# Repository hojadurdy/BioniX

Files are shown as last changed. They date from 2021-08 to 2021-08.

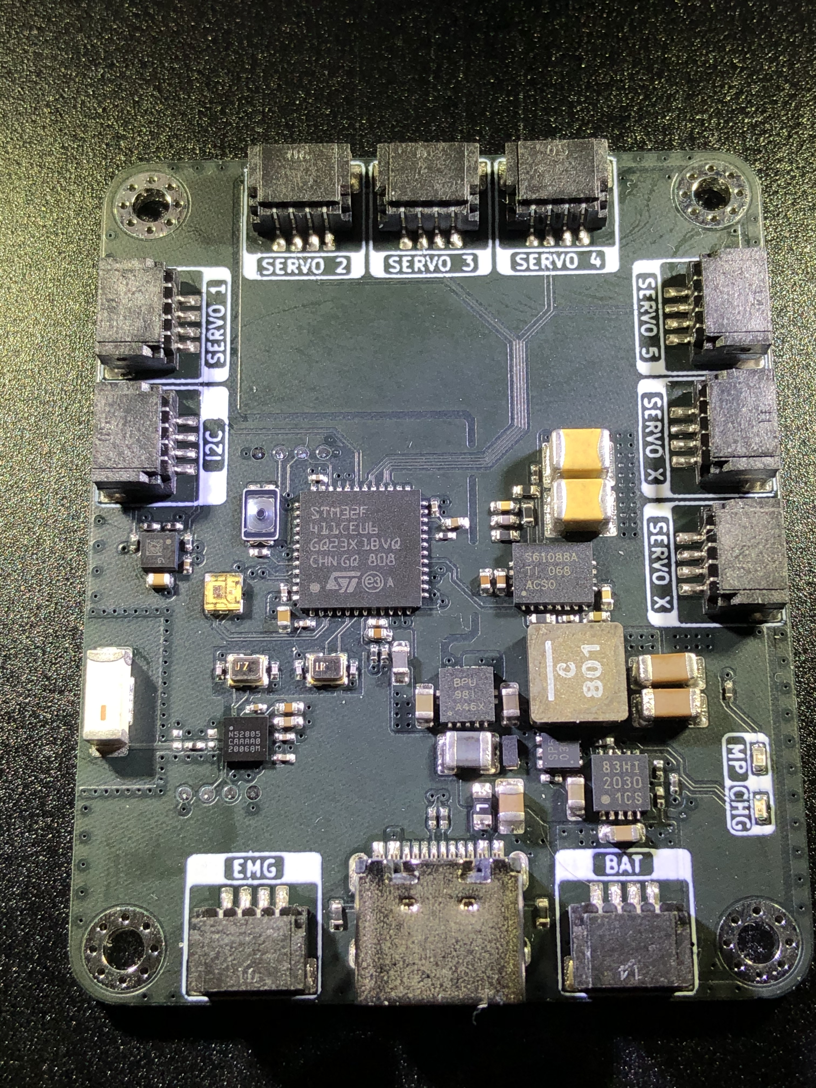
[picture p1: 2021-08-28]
Photo/IMG_0271.jpeg

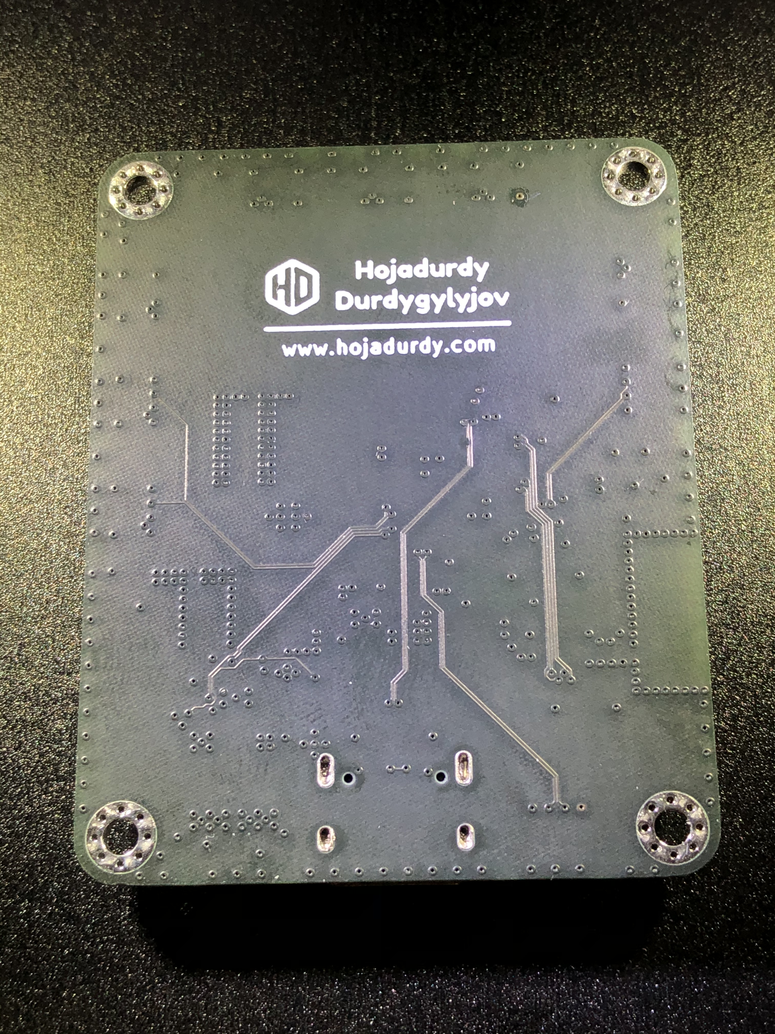
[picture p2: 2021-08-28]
Photo/IMG_0272.jpeg

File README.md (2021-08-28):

### BioniX
Controller board for a prototype robotic prosthetic hand. 

#Features

- 5 servo motors. 1 for each finger.
- 2 servo motors for wrist gimbal.
- Onboard accelerometer and gyro.
- nRF805 Bleetooth SoC to communicate with mobile app.
- 600mA Li-Ion battery charging.
- 3.3V@1A Buck-Boost converter for EMG sensor and for the rest of the board.
- 6V@4A Boost converter for servos.

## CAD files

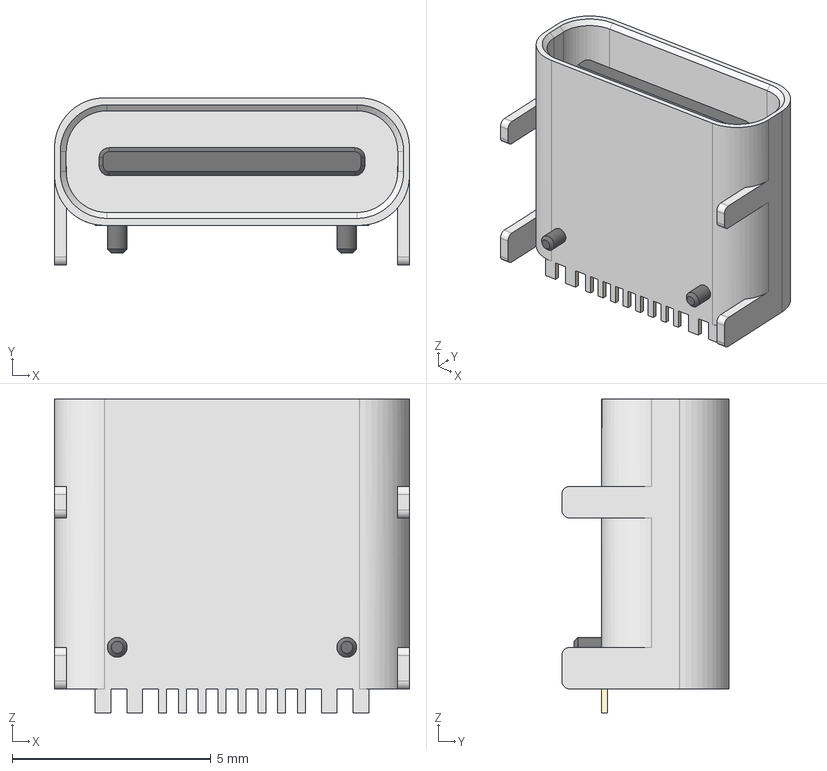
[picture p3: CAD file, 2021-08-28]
3D/TYPE-C Female Connector.step
8.94 x 4.21 x 7.90 mm

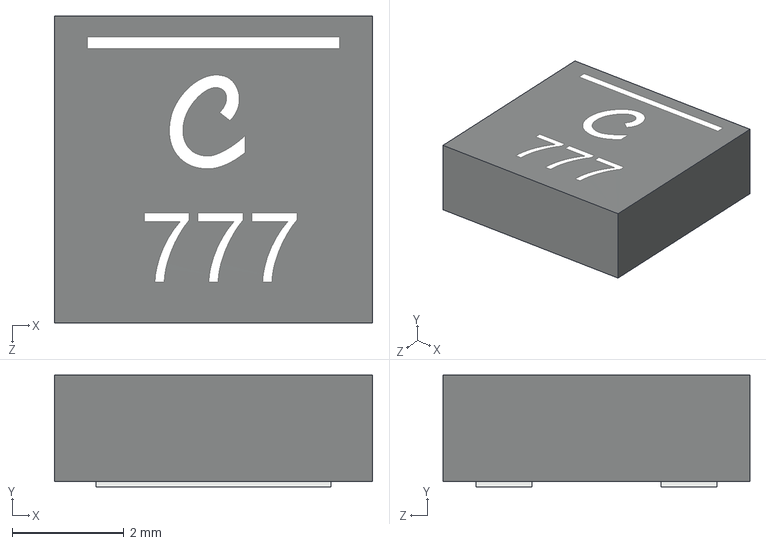
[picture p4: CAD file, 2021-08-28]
3D/Coilcraft-XAL5020.step
5.68 x 2.00 x 5.48 mm

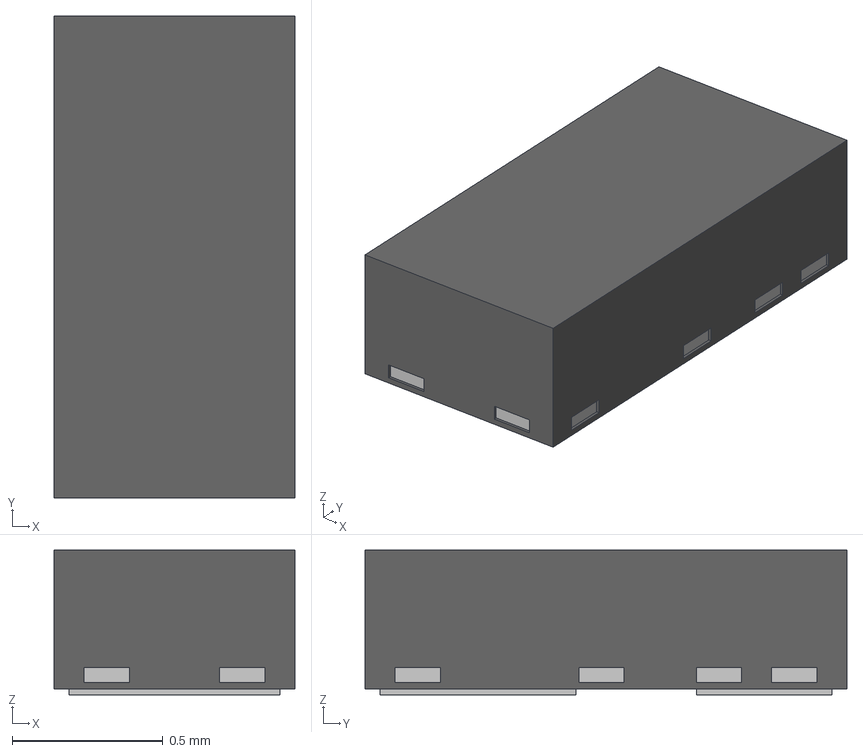
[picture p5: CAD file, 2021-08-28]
3D/CST2C.STEP
0.8 x 1.60 x 0.48 mm

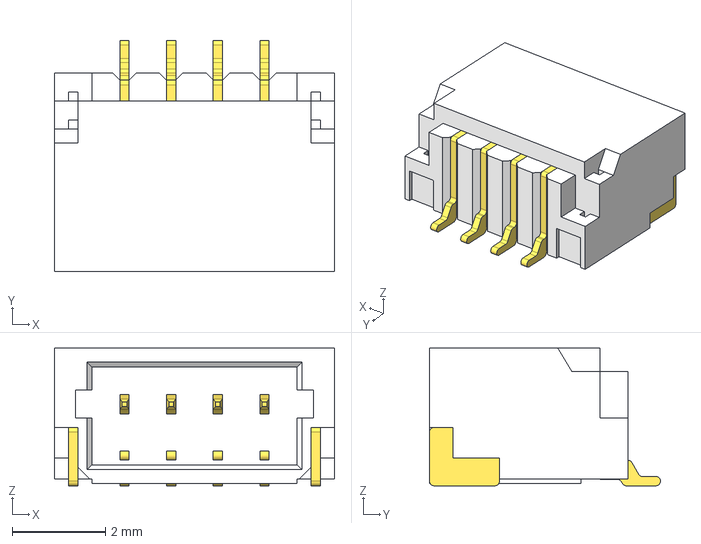
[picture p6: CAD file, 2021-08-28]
3D/JST-SH_4Pin_P1mm.step
6.00 x 4.95 x 2.95 mm

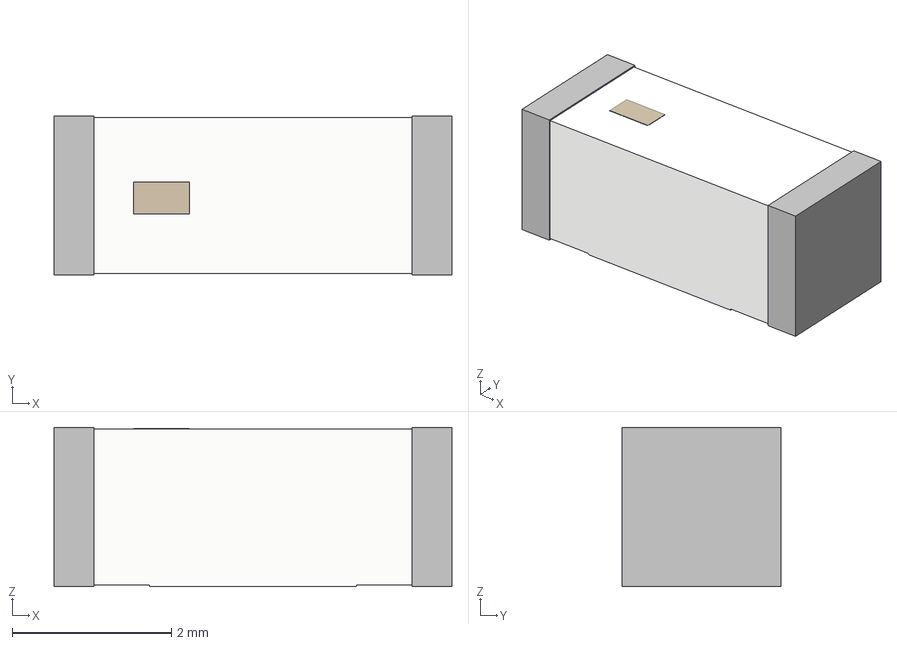
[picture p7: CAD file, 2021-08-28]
3D/2450AT42B100E.step
5.00 x 2.00 x 2.00 mm

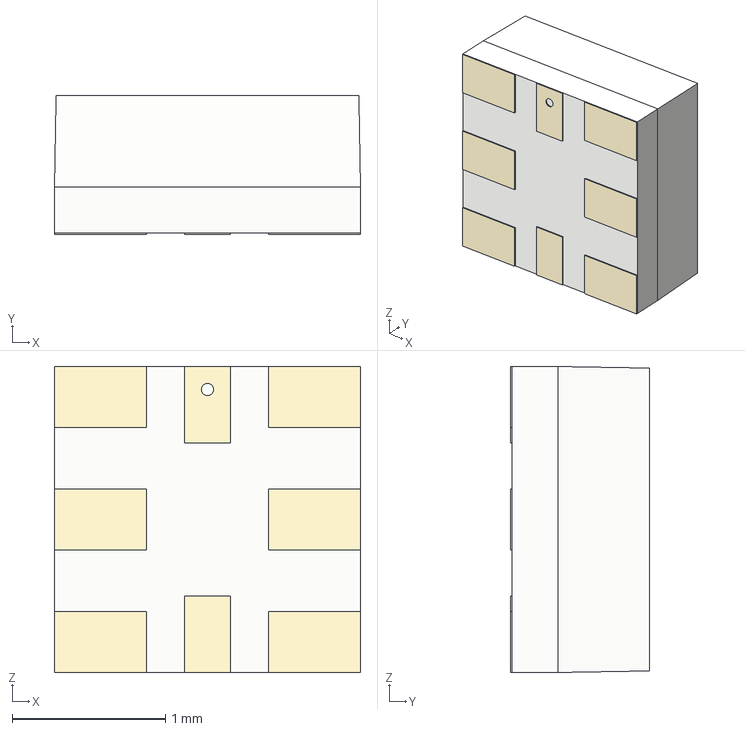
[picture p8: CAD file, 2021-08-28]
3D/APA102 2020 LED.step
2.00 x 0.91 x 2.00 mm

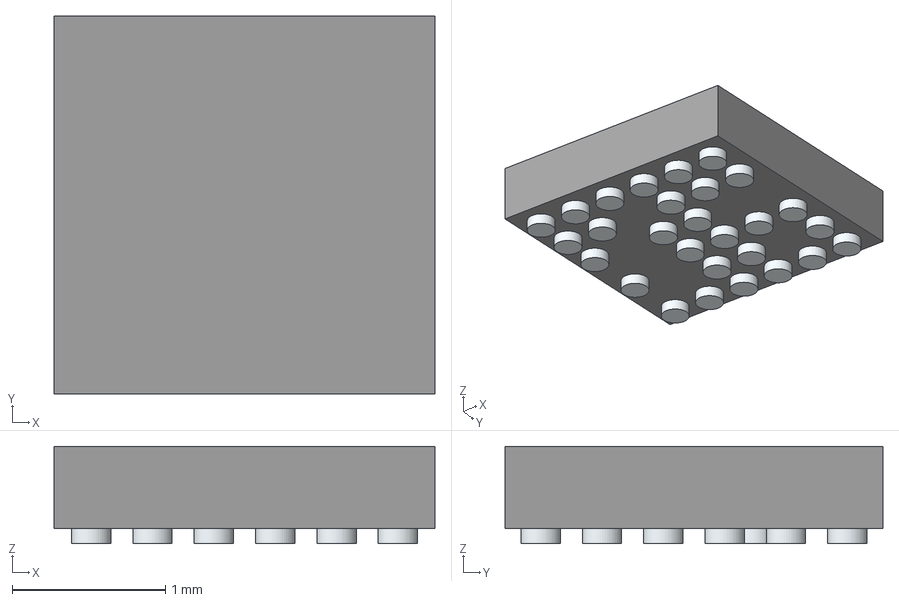
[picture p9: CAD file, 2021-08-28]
3D/NRF52805-CAAA.step
2.48 x 2.46 x 0.635 mm
Pins

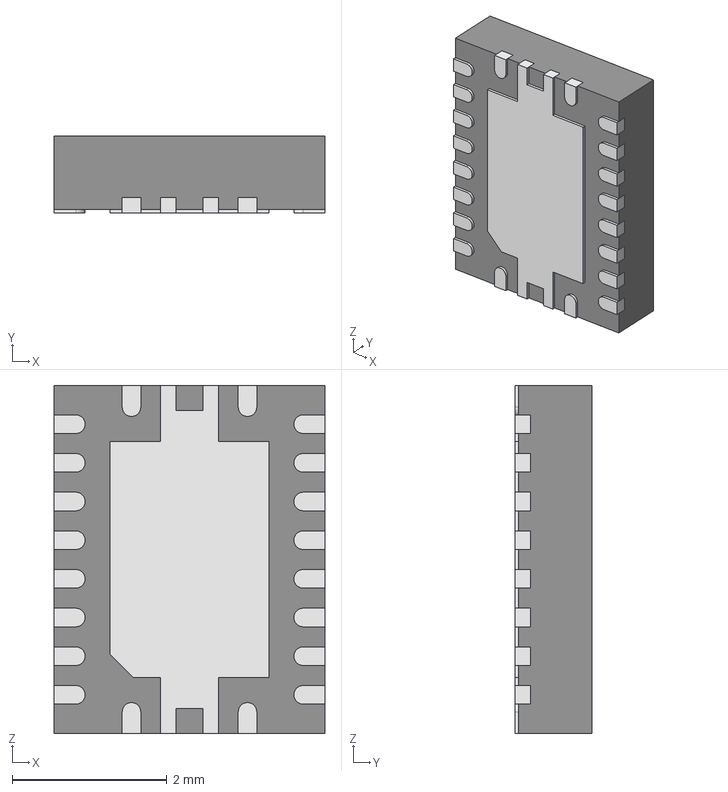
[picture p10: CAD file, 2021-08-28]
3D/TPS61088RHLT.STEP
3.50 x 1.00 x 4.50 mm

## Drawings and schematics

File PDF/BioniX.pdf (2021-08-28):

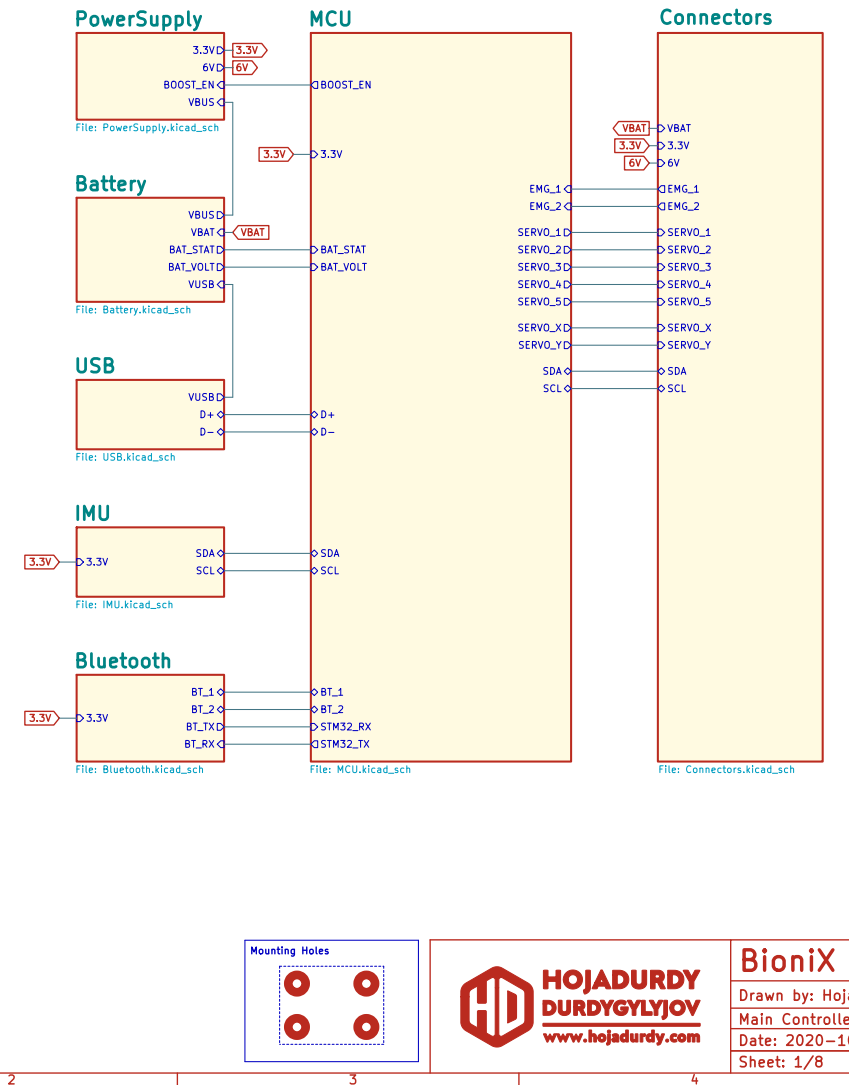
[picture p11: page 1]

File: BioniX.kicad_sch Sheet: 1/8 Drawn by: Hojadurdy Durdygylyjov Main Controller Board for BioniX Prosthetic Arm with Linear Actuators. License: CC Attribution-ShareAlike 4.0 International MCU
BAT_VOLT BAT_STAT
SCL VUSB
File: USB.kicad_sch Bluetooth

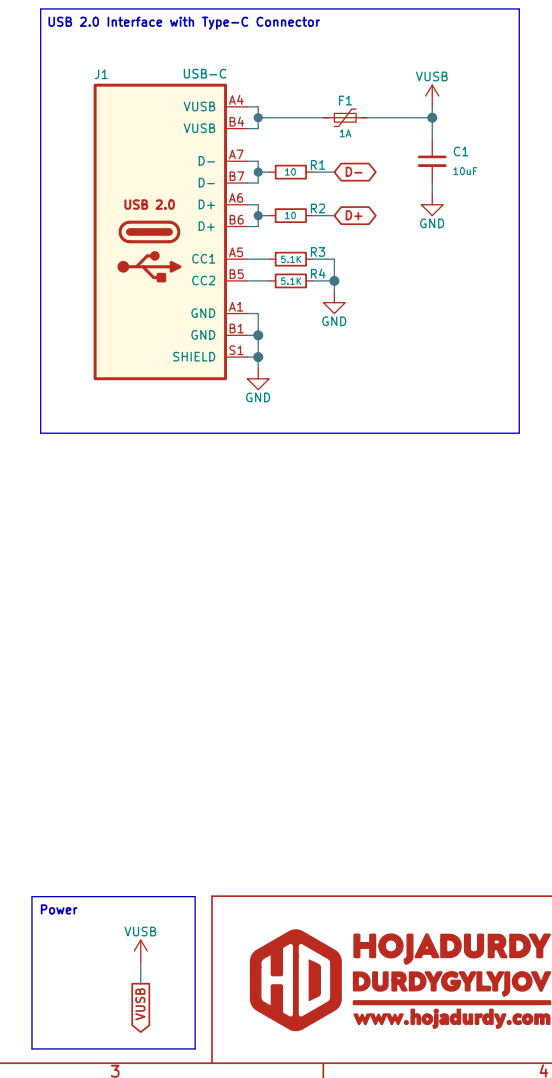
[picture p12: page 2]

USB 2.0 Interface with Type-C Connector
R1 10 GND
D- D+ Power

File: USB.kicad_sch Sheet: 2/8 Drawn by: Hojadurdy Durdygylyjov
USB 2.0 Interface with Type-C Connector License: CC Attribution-ShareAlike 4.0 International

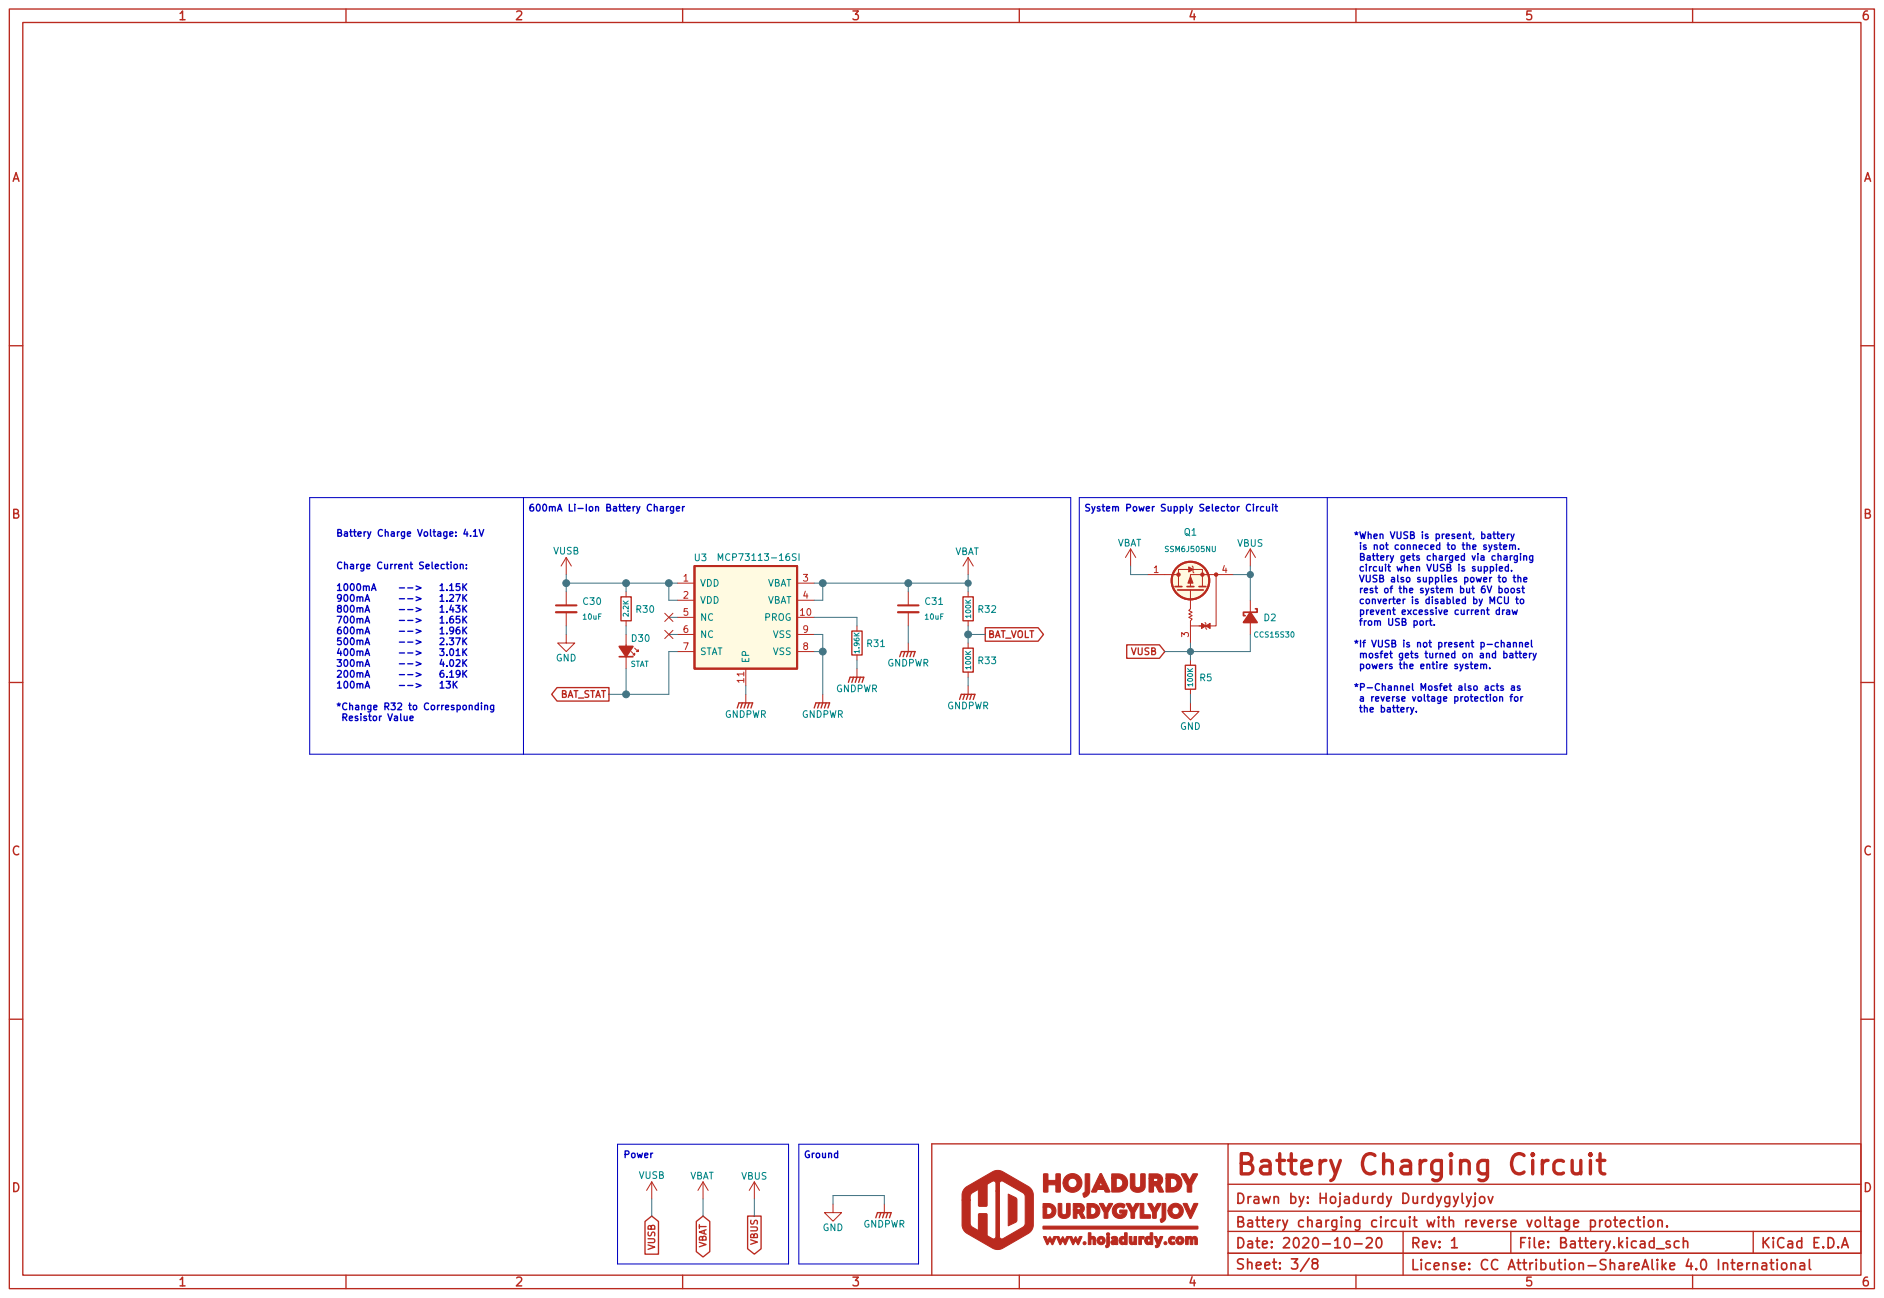
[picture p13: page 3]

the battery. 600mA Li-Ion Battery Charger Power

Battery Charge Voltage: 4.1V Charge Current Selection: 1000mA --> 1.15K

is not conneced to the system.
Battery gets charged via charging
circuit when VUSB is suppied.
VUSB also supplies power to the
rest of the system but 6V boost
converter is disabled by MCU to
prevent excessive current draw
from USB port. *If VUSB is not present p-channel

mosfet gets turned on and battery
powers the entire system. *P-Channel Mosfet also acts as

a reverse voltage protection for

File: Battery.kicad_sch Sheet: 3/8 Drawn by: Hojadurdy Durdygylyjov
Battery charging circuit with reverse voltage protection. License: CC Attribution-ShareAlike 4.0 International

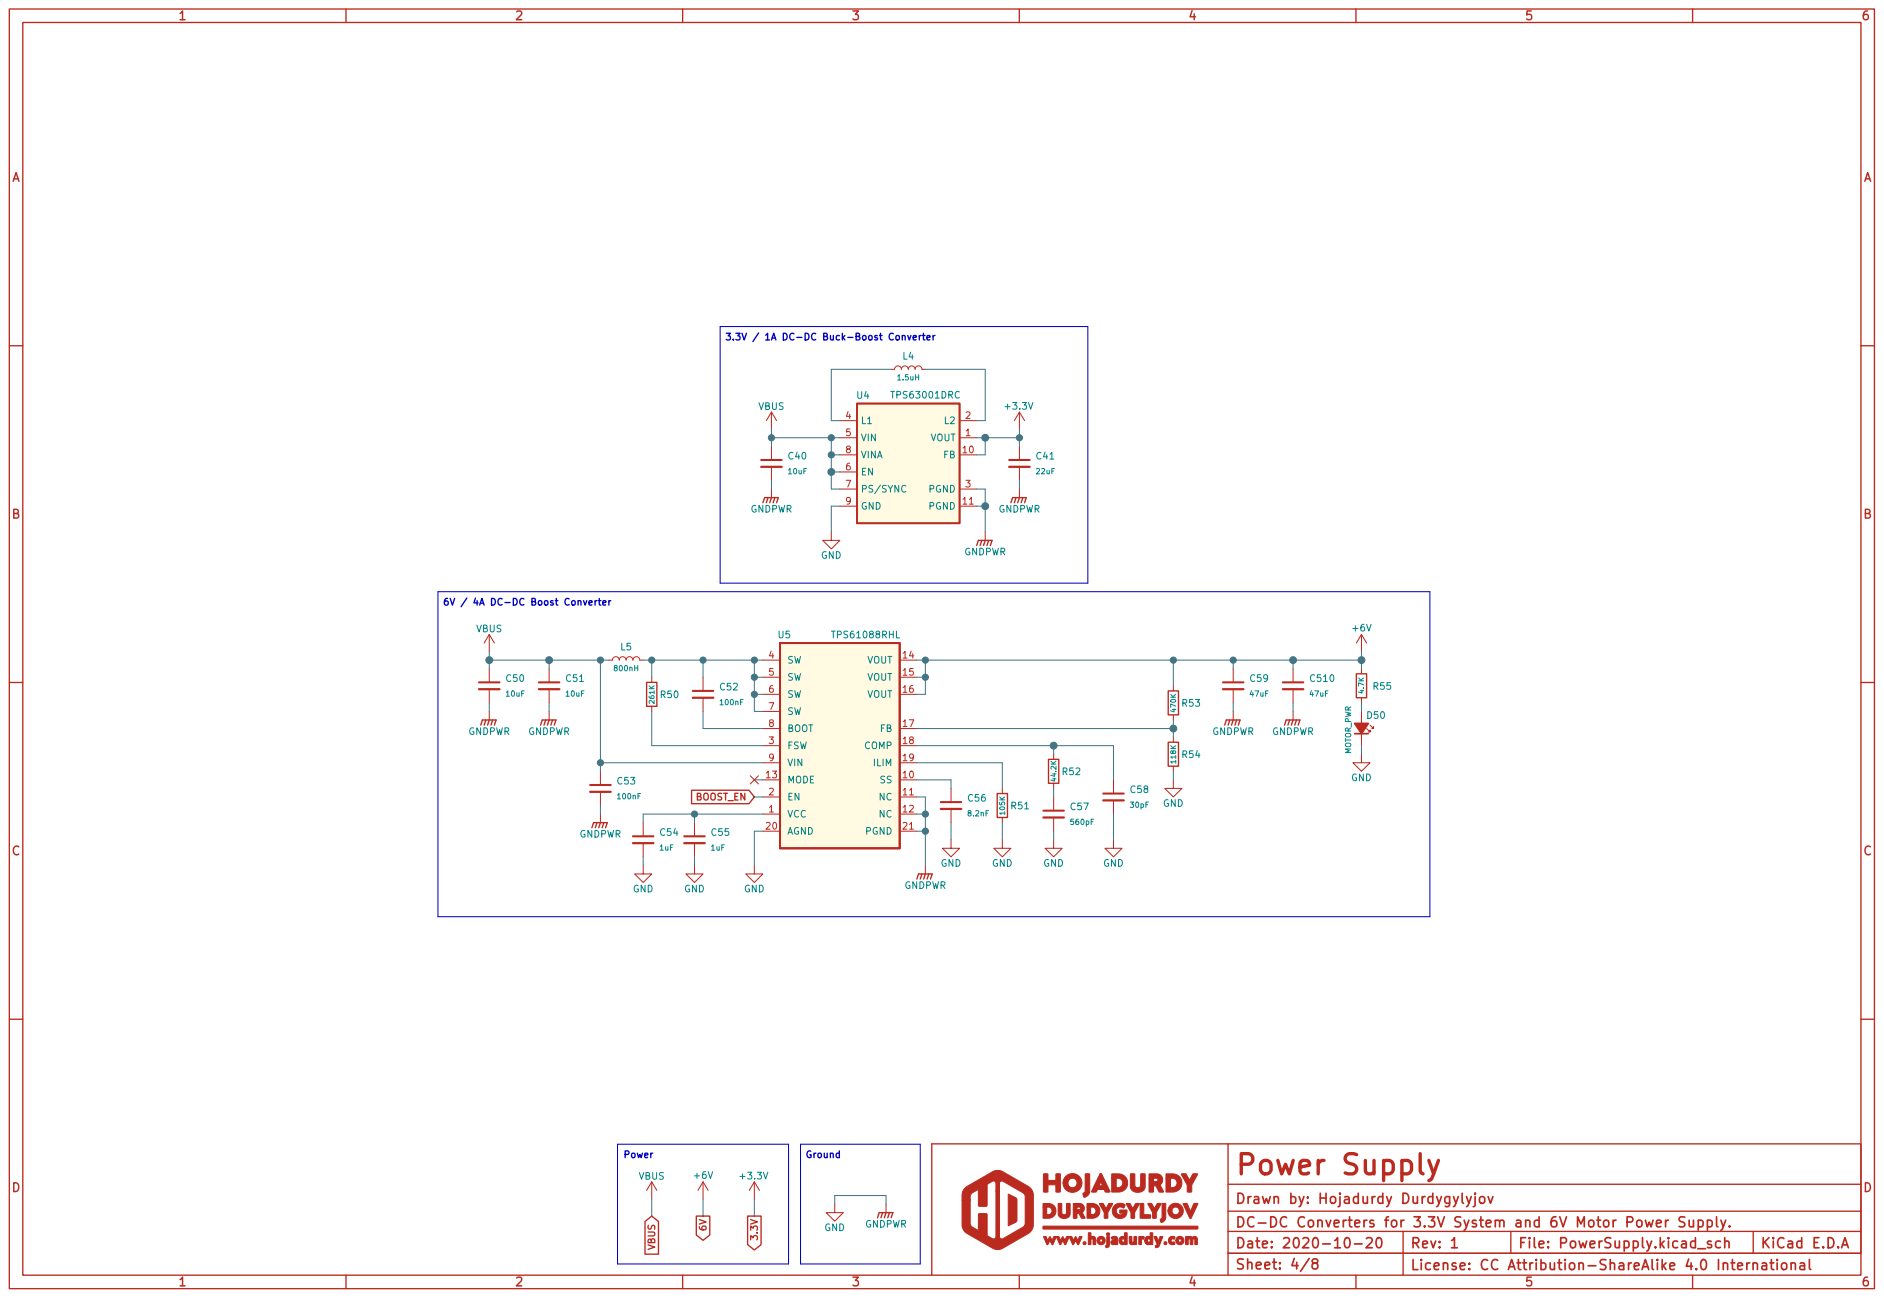
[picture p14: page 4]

File: PowerSupply.kicad_sch Sheet: 4/8 Drawn by: Hojadurdy Durdygylyjov

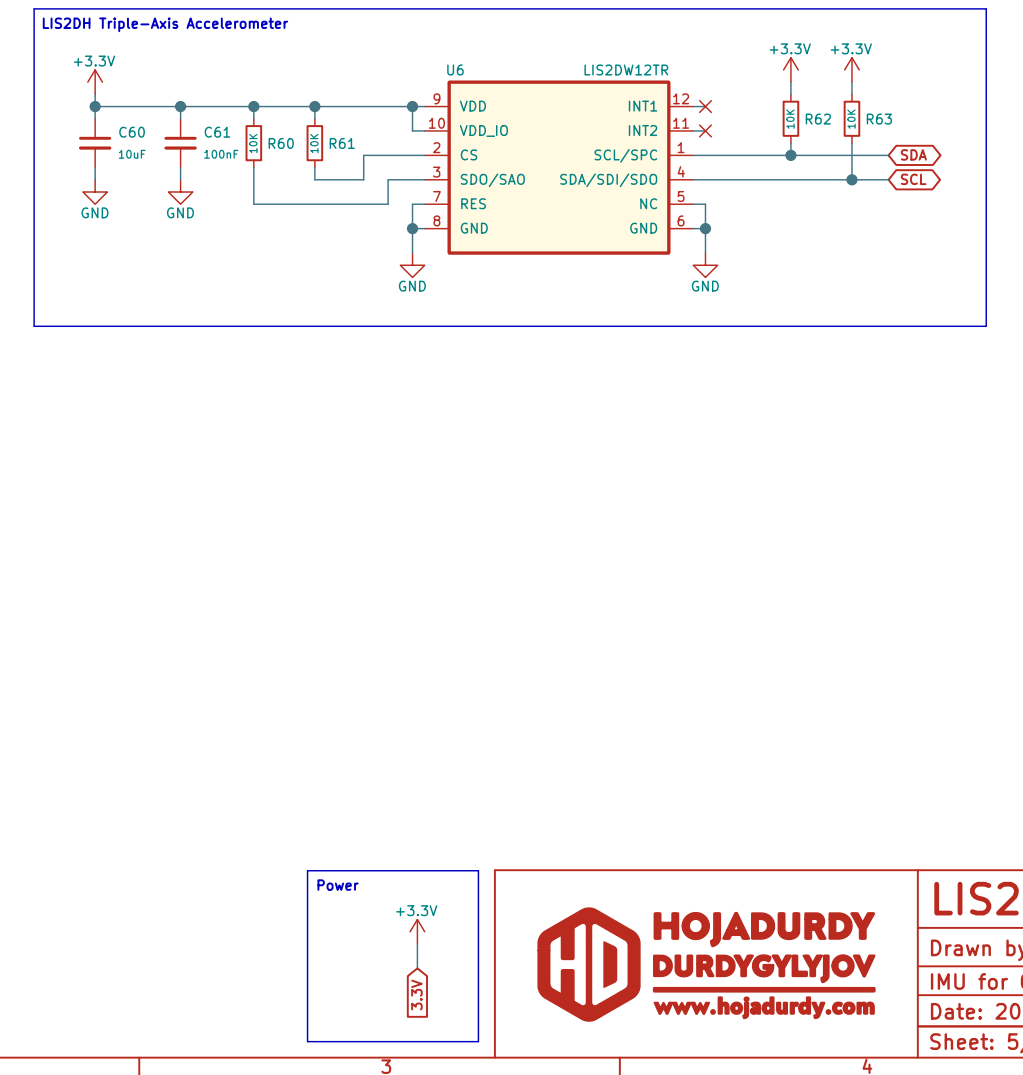
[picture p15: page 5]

File: IMU.kicad_sch Sheet: 5/8 Drawn by: Hojadurdy Durdygylyjov
IMU for Orientation and Motion Detection. License: CC Attribution-ShareAlike 4.0 International

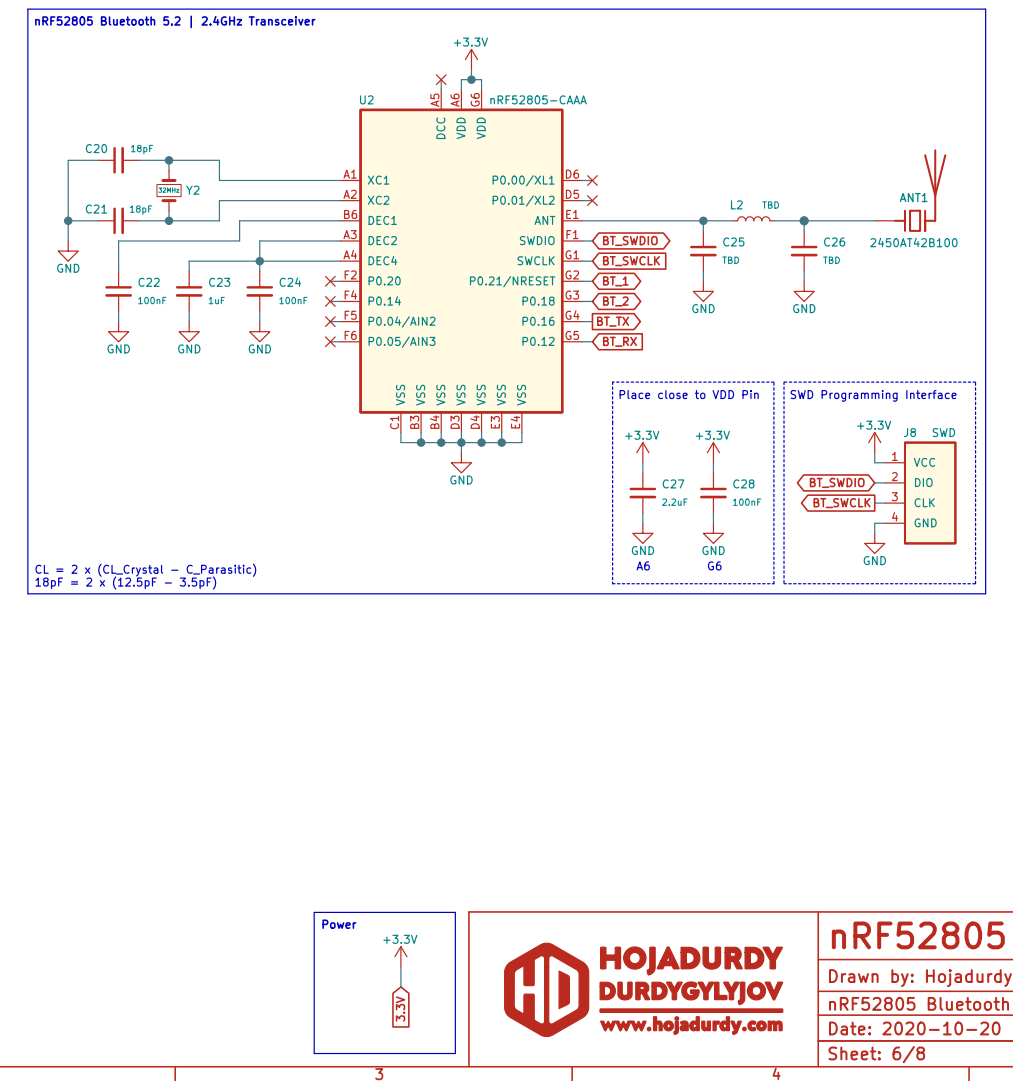
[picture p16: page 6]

File: Bluetooth.kicad_sch Sheet: 6/8 Drawn by: Hojadurdy Durdygylyjov
nRF52805 Bluetooth 5.2 | 2.4GHz Transceiver License: CC Attribution-ShareAlike 4.0 International

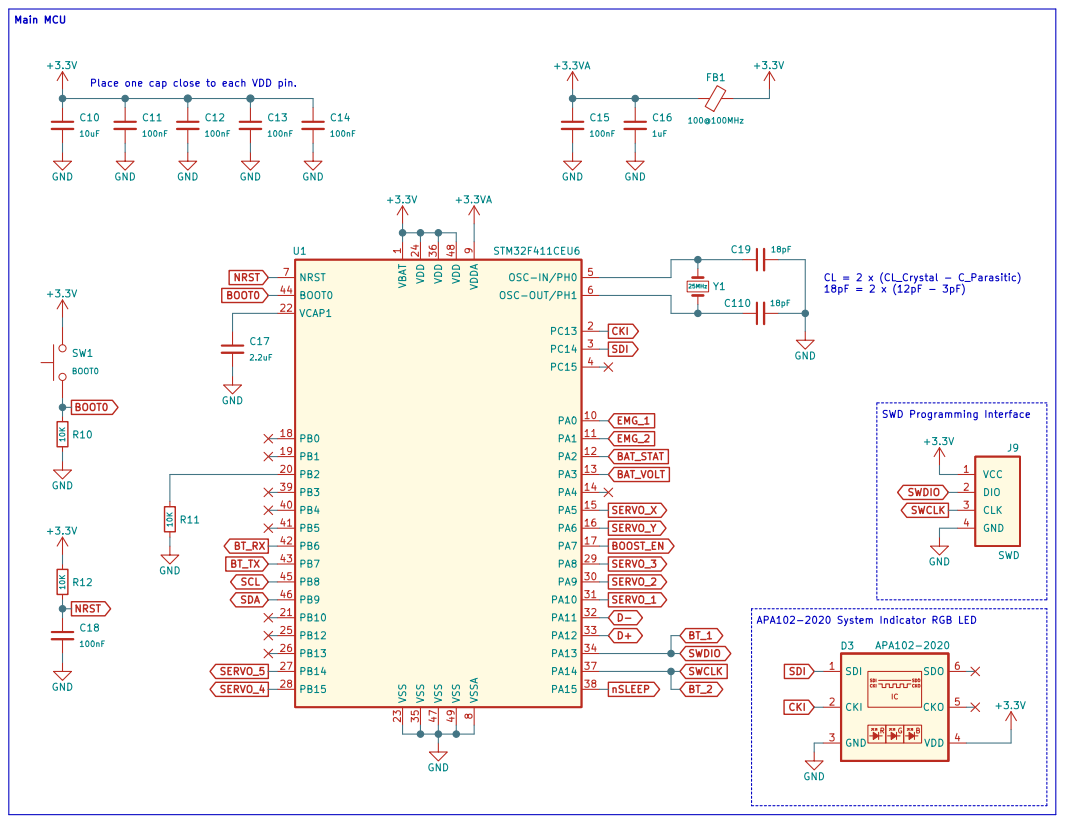
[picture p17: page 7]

1 VCAP1 22 VDD 24 VDD 36 VDD 48 VDDA

9 VSS 23 VSS 35 VSS 47 VSS 49 VSSA

License: CC Attribution-ShareAlike 4.0 International C18

File: MCU.kicad_sch Sheet: 7/8 Drawn by: Hojadurdy Durdygylyjov
STM32F411CE controls the entire system

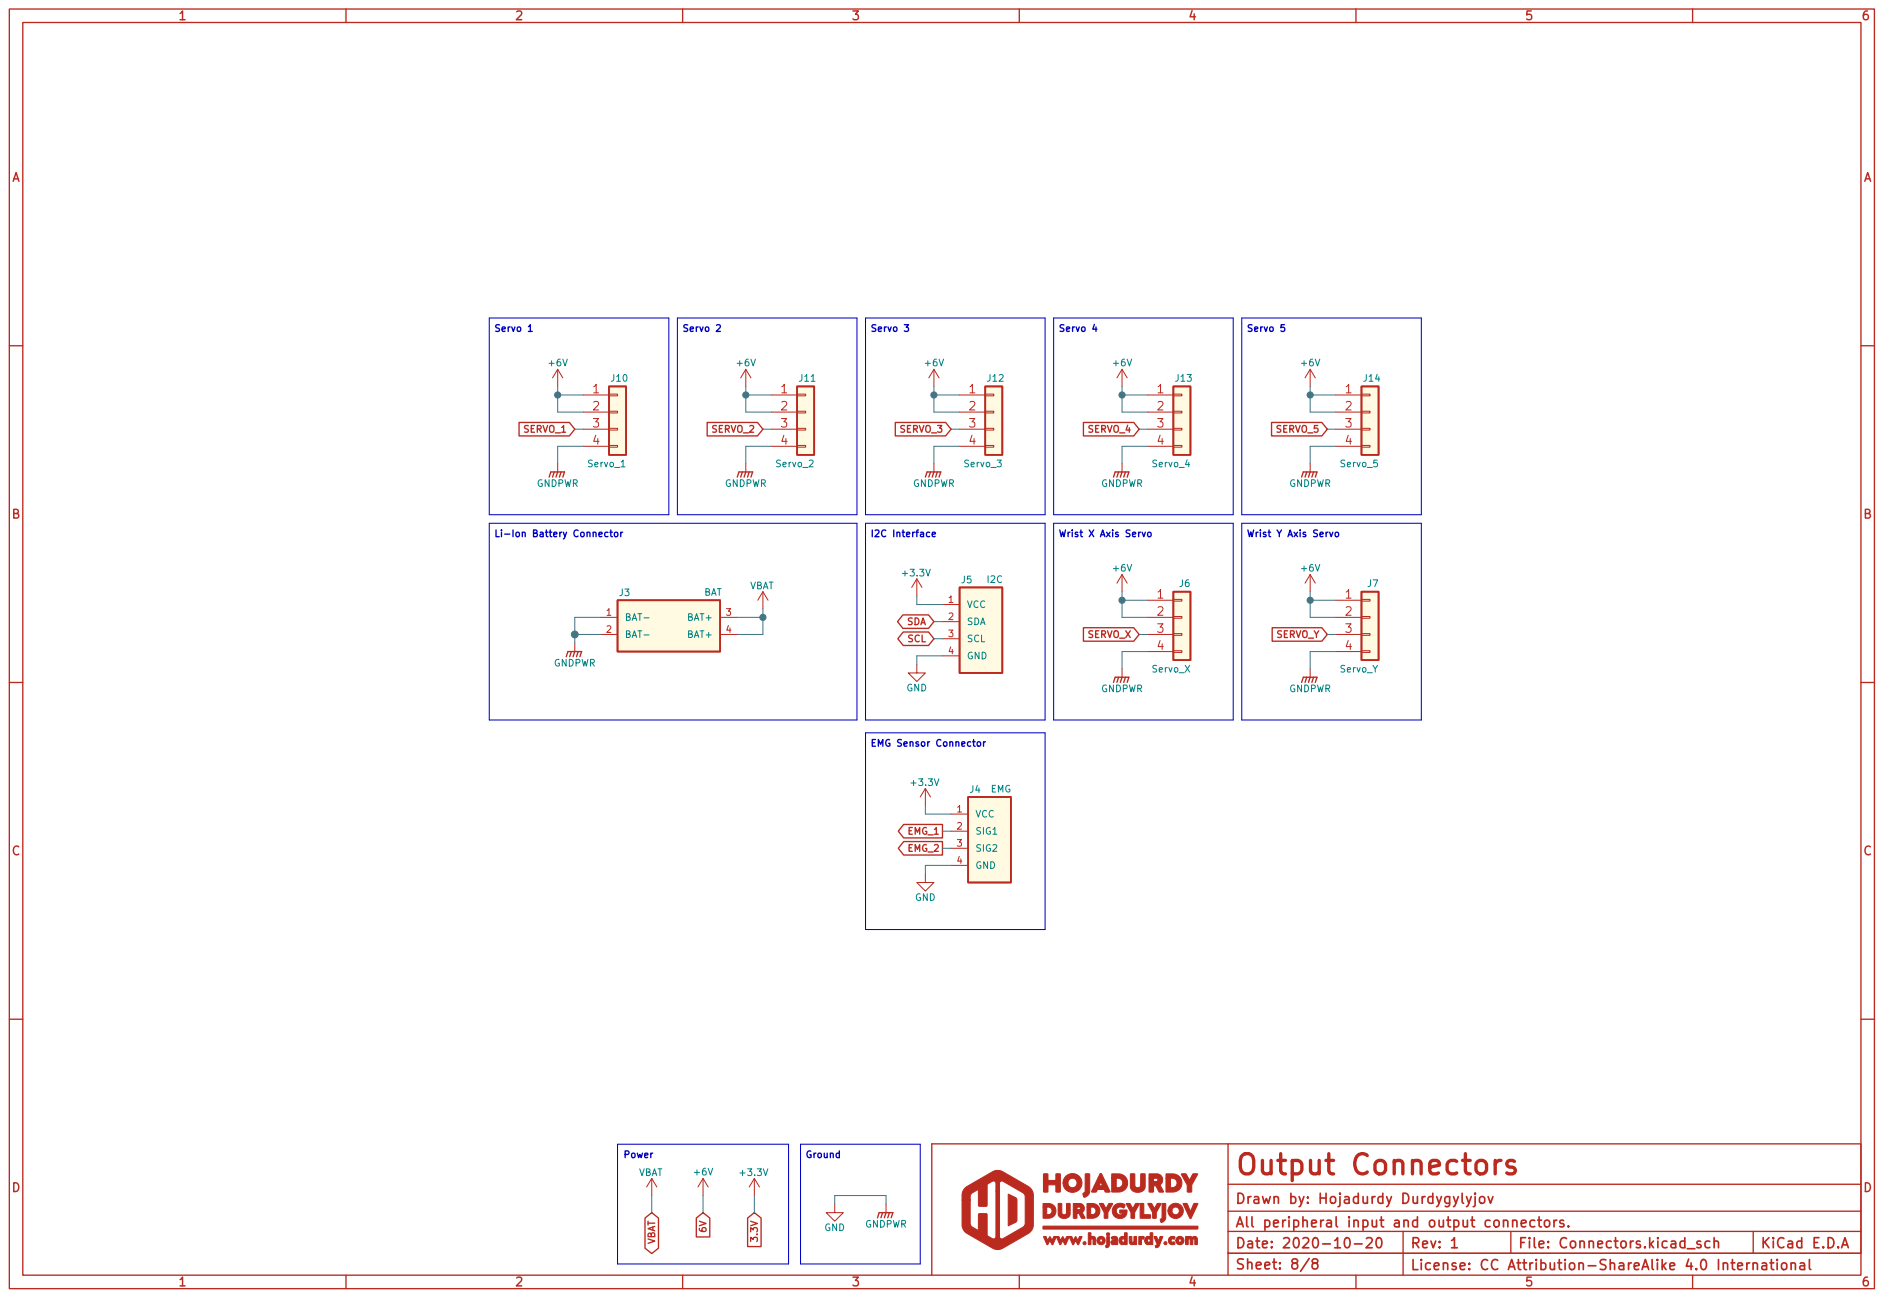
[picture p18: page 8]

File: Connectors.kicad_sch Sheet: 8/8 Drawn by: Hojadurdy Durdygylyjov

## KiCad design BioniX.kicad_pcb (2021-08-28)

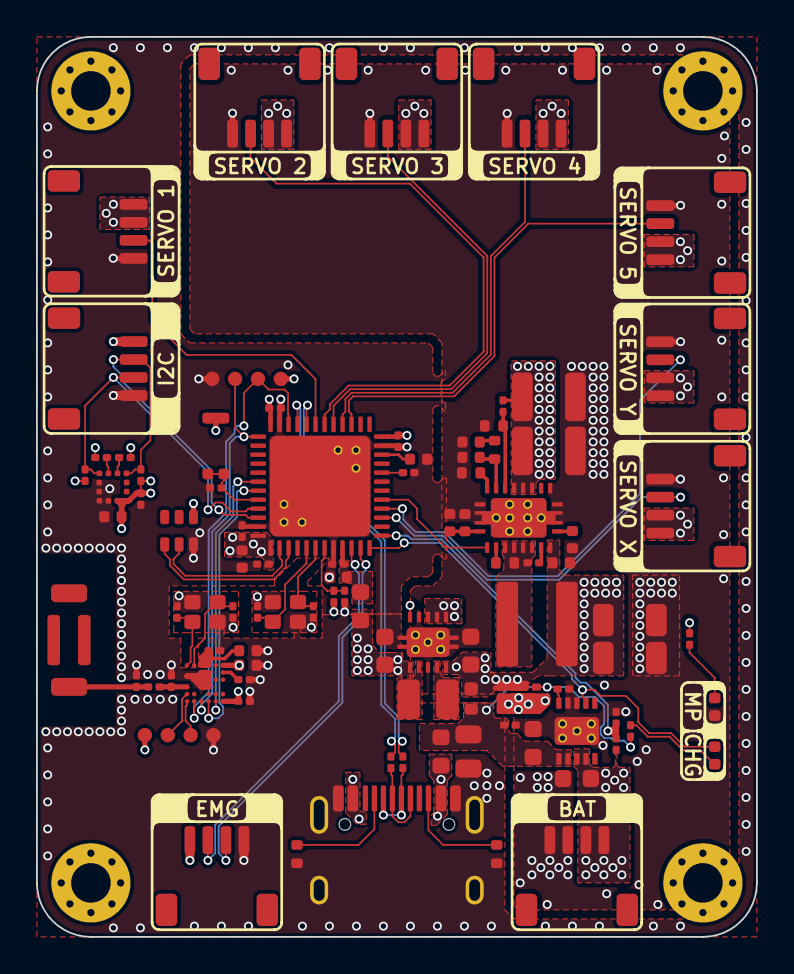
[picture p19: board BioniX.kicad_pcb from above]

Board: 4 copper layers, 40.0 x 50.0 mm, 97 parts (0 on the bottom side), 64 nets.

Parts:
ANT1: 2450AT42B100; 2450AT42B100E
C1: 10uF; C_0805_2012Metric
C10, C60: 10uF; C_0402_1005Metric
C11, C12, C13, C14, C15, C18, C22, C24, C28, C52, C61: 100nF; C_0201_0603Metric
C16, C23, C54, C55: 1uF; C_0402_1005Metric
C17, C27: 2.2uF; C_0402_1005Metric
C19, C20, C21, C110: 18pF; C_0201_0603Metric
C25, C26: TBD; C_0201_0603Metric
C30, C31, C40: 10uF; C_0603_1608Metric
C41: 22uF; C_0603_1608Metric
C50, C51: 10uF; C_1206_3216Metric
C53: 100nF; C_0402_1005Metric
C56: 8.2nF; C_0402_1005Metric
C57: 560pF; C_0402_1005Metric
C58: 30pF; C_0402_1005Metric
C59, C510: 47uF; C_1210_3225Metric
D2: CCS15S30; CST2C
D3: APA102-2020
D30: STAT; LED_0402_1005Metric
D50: MOTOR_PWR; LED_0402_1005Metric
F1: 1A; Fuse_0603_1608Metric
FB1: 100@100MHz; L_0603_1608Metric
H1, H2, H3, H4: MountingHole; MountingHole_2.2mm_M2_Pad_Via
J1: USB-C; USB2.0_Type-C_Connector
J3: BAT; JST_SH_SM04B-SRSS-TB_1x04-1MP_P1.00mm_Horizontal
J4: EMG; JST_SH_SM04B-SRSS-TB_1x04-1MP_P1.00mm_Horizontal
J5: I2C; JST_SH_SM04B-SRSS-TB_1x04-1MP_P1.00mm_Horizontal
J6: Servo_X; JST_SH_SM04B-SRSS-TB_1x04-1MP_P1.00mm_Horizontal
J7: Servo_Y; JST_SH_SM04B-SRSS-TB_1x04-1MP_P1.00mm_Horizontal
J8, J9: SWD; SWD_Pogo_Pad
J10: Servo_1; JST_SH_SM04B-SRSS-TB_1x04-1MP_P1.00mm_Horizontal
J11: Servo_2; JST_SH_SM04B-SRSS-TB_1x04-1MP_P1.00mm_Horizontal
J12: Servo_3; JST_SH_SM04B-SRSS-TB_1x04-1MP_P1.00mm_Horizontal
J13: Servo_4; JST_SH_SM04B-SRSS-TB_1x04-1MP_P1.00mm_Horizontal
J14: Servo_5; JST_SH_SM04B-SRSS-TB_1x04-1MP_P1.00mm_Horizontal
L2: TBD; L_0201_0603Metric
L4: 1.5uH; L_1008_2520Metric
L5: 800nH; L_Coilcraft_XAL5030
Q1: SSM6J505NU; UDFN2020-6
R1, R2: 10; R_0201_0603Metric
R3, R4: 5.1K; R_0402_1005Metric
R5, R32, R33: 100K; R_0201_0603Metric
R10, R11, R12, R60, R61, R62, R63: 10K; R_0201_0603Metric
R30: 2.2K; R_0201_0603Metric
R31: 1.96K; R_0201_0603Metric
R50: 261K; R_0402_1005Metric
R51: 105K; R_0402_1005Metric
R52: 44.2K; R_0402_1005Metric
R53: 470K; R_0201_0603Metric
R54: 118K; R_0402_1005Metric
R55: 4.7K; R_0201_0603Metric
SW1: BOOT0; MicroSwitch
U1: STM32F411CEU6; QFN-48-1EP_7x7mm_P0.5mm_EP5.6x5.6mm
U2: nRF52805-CAAA; NRF52805-CAAA
U3: MCP73113-16SI; DFN-10-1EP_3x3mm_P0.5mm_EP1.55x2.48mm
U4: TPS63001DRC; Texas_VSON-10_3x3mm_P0.5mm
U5: TPS61088RHL; Texas_VQFN-RHL-20
U6: LIS2DW12TR; LGA-12_2x2mm_P0.5mm
Y1: 25MHz; Crystal_SMD_2016-4Pin_2.0x1.6mm
Y2: 32MHz; Crystal_SMD_2016-4Pin_2.0x1.6mm

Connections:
3.3V: C10.1, C11.1, C12.1, C13.1, C14.1, C27.1, C28.1, C41.1, C60.1, C61.1, D3.4 (VDD), FB1.2, J4.1 (VCC), J5.1 (VCC), J8.1 (VCC), J9.1 (VCC), R12.2, R60.2, R61.2, R62.2, R63.2, SW1.2, U1.1 (VBAT), U1.24 (VDD), U1.36 (VDD), U1.48 (VDD), U2.A6 (VDD), U2.G6 (VDD), U4.1 (VOUT), U4.10 (FB), U6.9 (VDD), U6.10 (VDD_IO)
6V: C59.1, C510.1, J6.1, J6.2, J7.1, J7.2, J10.1, J10.2, J11.1, J11.2, J12.1, J12.2, J13.1, J13.2, J14.1, J14.2, R53.1, R55.2, U5.14 (VOUT), U5.15 (VOUT), U5.16 (VOUT)
+3.3VA: C15.1, C16.1, FB1.1, U1.9 (VDDA)
BAT_STAT: D30.1 (K), U1.12 (PA2), U3.7 (STAT)
BAT_VOLT: R32.1, R33.2, U1.13 (PA3)
BOOST_EN: U1.17 (PA7), U5.2 (EN)
BOOT0: R10.2, SW1.1, U1.44 (BOOT0)
BT_1: J9.2 (DIO), U1.34 (PA13), U2.G2 (P0.21/NRESET)
BT_2: J9.3 (CLK), U1.37 (PA14), U2.G3 (P0.18)
BT_RX: U1.42 (PB6), U2.G5 (P0.12)
BT_SWCLK: J8.3 (CLK), U2.G1 (SWCLK)
BT_SWDIO: J8.2 (DIO), U2.F1 (SWDIO)
BT_TX: U1.43 (PB7), U2.G4 (P0.16)
CKI: D3.2 (CKI), U1.2 (PC13)
D+: R2.2, U1.33 (PA12)
D-: R1.2, U1.32 (PA11)
EMG_1: J4.2 (SIG1), U1.10 (PA0)
EMG_2: J4.3 (SIG2), U1.11 (PA1)
GND: C1.2, C10.2, C11.2, C12.2, C13.2, C14.2, C15.2, C16.2, C17.2, C18.2, C19.2, C20.1, C21.1, C22.2, C23.2, C24.2, C25.2, C26.2, C27.2, C28.2, C30.2, C31.2, C40.2, C41.2, C50.2, C51.2, C53.2, C54.2, C55.2, C56.2, C57.2, C58.2, C59.2, C60.2, C61.2, C110.2, C510.2, D3.3 (GND), D50.1 (K), J1.A1 (GND), J1.B1 (GND), J1.S1 (SHIELD), J3.1 (BAT-), J3.2 (BAT-), J4.4 (GND), J5.4 (GND), J6.4, J7.4, J8.4 (GND), J9.4 (GND), J10.4, J11.4, J12.4, J13.4, J14.4, R3.2, R4.2, R5.1, R10.1, R11.1, R31.1, R33.1, R51.2, R54.2, U1.8 (VSSA), U1.23 (VSS), U1.35 (VSS), U1.47 (VSS), U1.49 (VSS), U2.B3 (VSS), U2.B4 (VSS), U2.C1 (VSS), U2.D3 (VSS), U2.D4 (VSS), U2.E3 (VSS), U2.E4 (VSS), U3.8 (VSS), U3.9 (VSS), U3.11 (EP), U4.3 (PGND), U4.9 (GND), U4.11 (PGND), U5.11 (NC), U5.12 (NC), U5.20 (AGND), U5.21 (PGND), U6.5 (NC), U6.6 (GND), U6.7 (RES), U6.8 (GND), Y1.2, Y1.4, Y2.2, Y2.4
NRST: C18.1, R12.1, U1.7 (NRST)
unnamed: ANT1.1 (FEED), C26.1, L2.1
unnamed: C17.1, U1.22 (VCAP1)
unnamed: C19.1, U1.5 (OSC-IN/PH0), Y1.3
unnamed: C20.2, U2.A1 (XC1), Y2.3
unnamed: C21.2, U2.A2 (XC2), Y2.1
unnamed: C22.1, U2.B6 (DEC1)
unnamed: C23.1, C24.1, U2.A3 (DEC2), U2.A4 (DEC4)
unnamed: C25.1, L2.2, U2.E1 (ANT)
unnamed: C52.1, L5.2, R50.1, U5.4 (SW), U5.5 (SW), U5.6 (SW), U5.7 (SW)
unnamed: C52.2, U5.8 (BOOT)
unnamed: C54.1, C55.1, U5.1 (VCC)
unnamed: C56.1, U5.10 (SS)
unnamed: C57.1, R52.2
unnamed: C58.1, R52.1, U5.18 (COMP)
unnamed: C110.1, U1.6 (OSC-OUT/PH1), Y1.1
unnamed: D30.2 (A), R30.1
unnamed: D50.2 (A), R55.1
unnamed: F1.1, J1.A4 (VUSB), J1.B4 (VUSB)
unnamed: J1.A5 (CC1), R3.1
unnamed: J1.A6 (D+), J1.B6 (D+), R2.1
unnamed: J1.A7 (D-), J1.B7 (D-), R1.1
unnamed: J1.B5 (CC2), R4.1
unnamed: L4.1, U4.4 (L1)
unnamed: L4.2, U4.2 (L2)
unnamed: R11.2, U1.20 (PB2)
unnamed: R31.2, U3.10 (PROG)
unnamed: R50.2, U5.3 (FSW)
unnamed: R51.1, U5.19 (ILIM)
unnamed: R53.2, R54.1, U5.17 (FB)
unnamed: R60.1, U6.3 (SDO/SAO)
unnamed: R61.1, U6.2 (CS)
SCL: J5.3 (SCL), R63.1, U1.45 (PB8), U6.4 (SDA/SDI/SDO)
SDA: J5.2 (SDA), R62.1, U1.46 (PB9), U6.1 (SCL/SPC)
SDI: D3.1 (SDI), U1.3 (PC14)
SERVO_1: J10.3, U1.31 (PA10)
SERVO_2: J11.3, U1.30 (PA9)
SERVO_3: J12.3, U1.29 (PA8)
SERVO_4: J13.3, U1.28 (PB15)
SERVO_5: J14.3, U1.27 (PB14)
SERVO_X: J6.3, U1.15 (PA5)
SERVO_Y: J7.3, U1.16 (PA6)
VBAT: C31.1, J3.3 (BAT+), J3.4 (BAT+), Q1.1 (D), Q1.2 (D), Q1.5 (D), Q1.6 (D), Q1.7 (D), R32.2, U3.3 (VBAT), U3.4 (VBAT)
VBUS: C40.1, C50.1, C51.1, C53.1, D2.1 (K), L5.1, Q1.4 (S), Q1.8 (S), U4.5 (VIN), U4.6 (EN), U4.7 (PS/SYNC), U4.8 (VINA), U5.9 (VIN)
VUSB: C1.1, C30.1, D2.2 (A), F1.2, Q1.3 (G), R5.2, R30.2, U3.1 (VDD), U3.2 (VDD)
